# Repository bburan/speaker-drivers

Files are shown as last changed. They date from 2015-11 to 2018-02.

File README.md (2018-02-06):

# Speaker drivers (2 watt)

## Overview

This circuit can drive a small earphone speaker that requires up to 2 watts of power (e.g., 500 mA current into an 8 ohm speaker). 

* It has unity gain in a non-inverting configuration (the speakers we work with only require about 1V maximum to achieve the desired sound levels).
* High-pass input stage with 1.26 Hz cutoff (basically a DC filter).
* Two BUF634 in parallel to provide up to 500 mA of current.

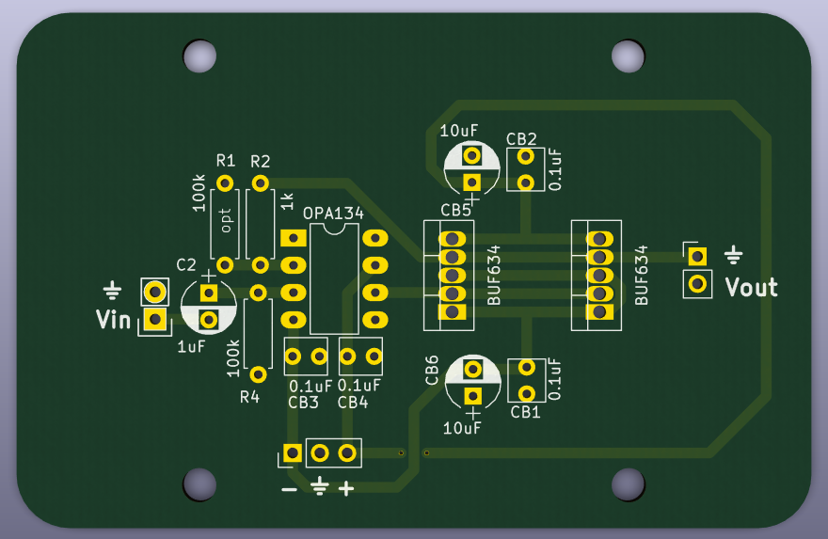
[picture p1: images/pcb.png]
Rendering of PCB


The board is 74mm x 48mm and the mounting holes, spaced 40mm x 40mm, are sized for a M3 screw. The board will fit in a Hammond enclosure that accomodates 75mm wide boards.

## Getting started

OSH Park will print and ship three of these boards for approximately $30. 

Order the parts from the [parts list](speaker%20drivers%20part%20list.md). If you get a heat sink, Aavid Thermalloy 577202B00000G should fit nicely in the space allowed.

Solder all components. Be sure to attach heat sinks to the current buffers.

Wash the board with dH<sub>2</sub>O.

## Notes

Previous iterations of the design had a high-pass filter on the output.  However, we have modified the current iteration such that the high-pass filter is found on the input stage. This allows us to eliminate bulky components (required to handle the large current) that take up a lot of space.

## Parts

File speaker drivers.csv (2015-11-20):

Reference | Value | Footprint | Datasheet
OPA1 | OPA2134 | Sockets_DIP:DIP-8__300_ELL
RL1 | 100k | Discret:R5
RL3 | 100k | Discret:R5
CLin1 | 1uF | Discret:C1
C2 | 0.1uFC | Discret:C1
C1 | 0.1uFC | Discret:C1
RR1 | 100k | Discret:R5
RR3 | 100k | Discret:R5
CRin1 | 1uF | Discret:C1
BUFR1 | BUF634 | LBHB:BUF634
CR1 | 10uFT | Capacitors_ThroughHole:Capacitor5x6RM2.5
CP3 | 0.1uFC | Discret:C1
CP2 | 10uFE | Capacitors_ThroughHole:Capacitor5x6RM2.5
CN3 | 0.1uFC | Discret:C1
CN2 | 10uFE | Capacitors_ThroughHole:Capacitor5x6RM2.5
CG2 | 10uFE | Capacitors_ThroughHole:Capacitor5x6RM2.5
RR2 | 5k | Discret:R5
RL2 | 5k | Discret:R5
BUFR2 | BUF634 | LBHB:BUF634
RR4 | 22 | Discret:R5
CR3 | 2uF | Discret:C1
LR1 | 100uH
CR2 | 10uFT | Capacitors_ThroughHole:Capacitor5x6RM2.5
BUFL1 | BUF634 | LBHB:BUF634
CL1 | 10uFT | Capacitors_ThroughHole:Capacitor5x6RM2.5
BUFL2 | BUF634 | LBHB:BUF634
RL4 | 22 | Discret:R5
CL3 | 2uF | Discret:C1
LL1 | 100uH
CL2 | 10uFT | Capacitors_ThroughHole:Capacitor5x6RM2.5
SIGIN1 | 4P_miniDIN
SER1 | 8P_miniDIN
Cvr1 | 0.33uF | Discret:C1
Cvr2 | 0.1uF | Discret:C1
SIGOUT1 | 4P_miniDIN
VREG1 | 78L05
VCTL1 | PGA2310
RS1 | 100k | Discret:R5
PWR1 | 4P_miniDIN_PWR
CR6 | 0.1uF | Discret:C1
CR5 | 0.1uF | Discret:C1
CL6 | 0.1uF | Discret:C1
CL5 | 0.1uF | Discret:C1

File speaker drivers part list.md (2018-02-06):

| References         | Number | Value         | Part number        | Note                  |
| ------------------ | ------ | ------------- | ------------------ | --------------------- |
| B1, B2             | 2      | BUF634        | BUF634T            | heat sink recommended |
| C2                 | 1      | 1uF           | MKS02-1/50/10      | metal film            |
| CB1, CB2, CB3, CB4 | 4      | 0.1uF         | RDER72A104K1S1H03A |                       |
| CB5, CB6           | 2      | 10uF          | TAP106M025SCS      | tantalum recommended  |
| J1, J2, J3, J4     | 4      | mounting hole |                    |                       |
| P1                 | 1      | 0.1" header   |                    |                       |
| P2                 | 1      | 0.1" header   |                    |                       |
| P3                 | 1      | 0.1" header   |                    |                       |
| R1, R4             | 2      | 100k          | YR1B100KCC         |                       |
| R2                 | 1      | 1k            | YR1B1K0CC          |                       |
| U1                 | 1      | OPA134        | OPA134PA           |                       |

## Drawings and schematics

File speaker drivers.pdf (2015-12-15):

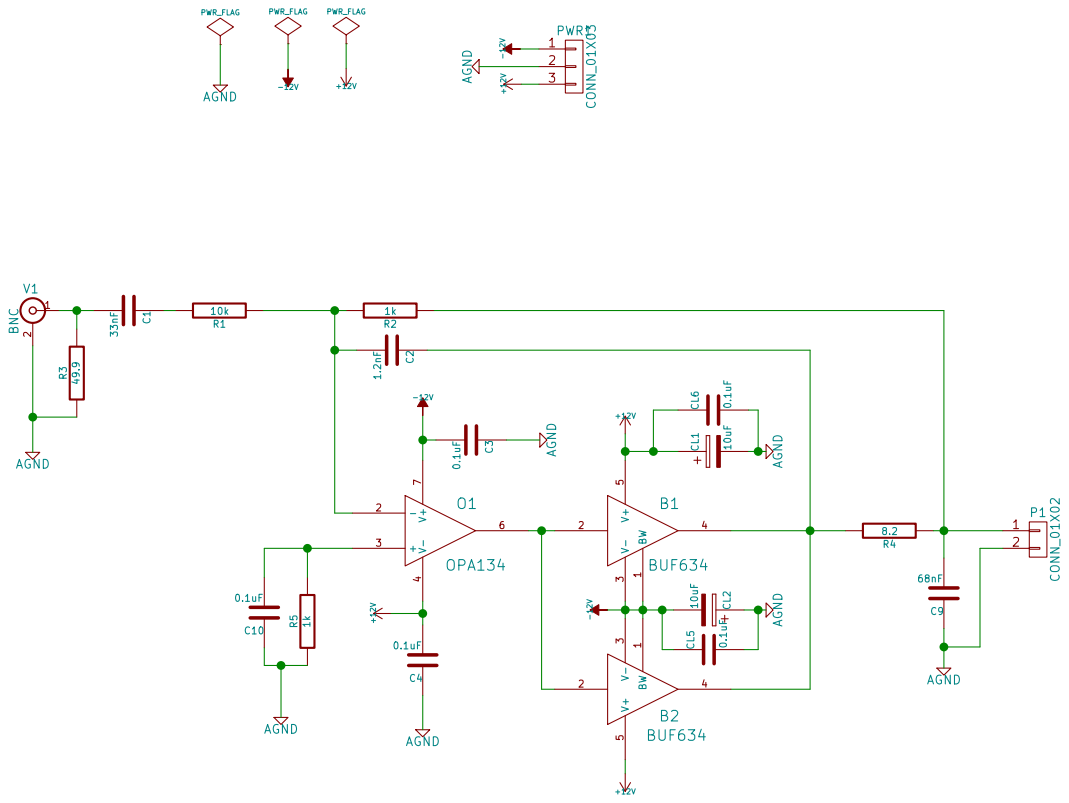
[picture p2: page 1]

This is licensed under GPLv3
File: speaker drivers.sch Sheet: / LBHB

Id: 1/1 Title: Dual Speaker Driver v2 with highpass filter

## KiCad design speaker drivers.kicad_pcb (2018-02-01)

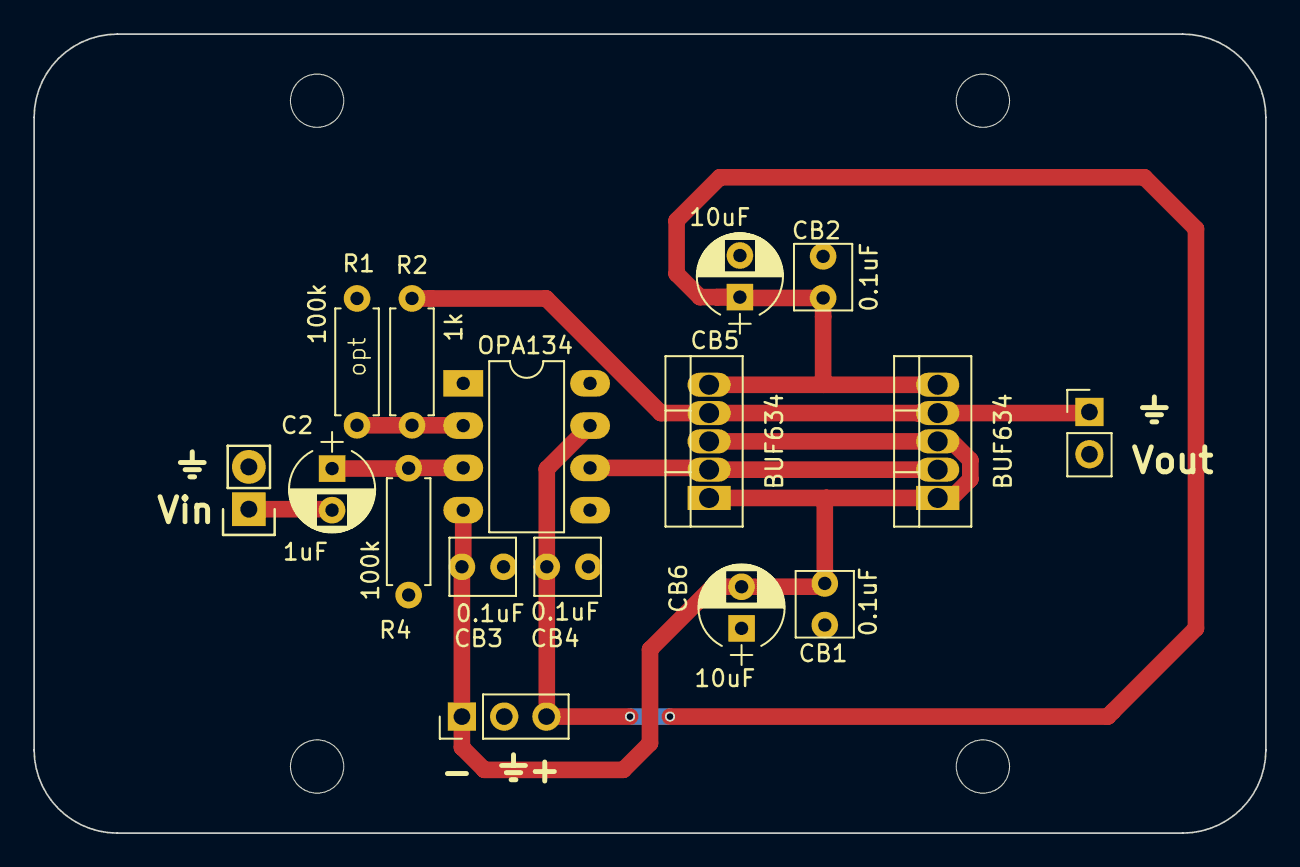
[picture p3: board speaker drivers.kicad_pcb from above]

Board: 2 copper layers, 74.0 x 48.0 mm, 20 parts (0 on the bottom side), 8 nets.

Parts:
B1: BUF634; BUF634T
B2: BUF634; TO-220-5_Vertical
C2: 1uF; CP_Radial_D5.0mm_P2.50mm
CB1, CB2, CB3, CB4: 0.1uF; C_Rect_L4.0mm_W3.5mm_P2.50mm
CB5, CB6: 10uF; CP_Radial_D5.0mm_P2.50mm
J1, J2, J3, J4: Conn_01x01; MountingHole_3.2mm_M3
P1: CONN_01X02; PinHeader_1x02_P2.54mm_Vertical
PWR1: CONN_01X03; PinHeader_1x03_P2.54mm_Vertical
R1, R4: 100k; R_Axial_DIN0207_L6.3mm_D2.5mm_P7.62mm_Horizontal
R2: 1k; R_Axial_DIN0207_L6.3mm_D2.5mm_P7.62mm_Horizontal
U1: OPA134; DIP-8_W7.62mm_LongPads
V1: BNC; Socket_Strip_Straight_1x02

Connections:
+12V: B1.5, B2.5, CB2.1, CB4.2, CB5.1, PWR1.3, U1.7
-12V: B1.1, B1.3, B2.1, B2.3, CB1.1, CB3.2, CB6.2, PWR1.1, U1.4
AGND: CB1.2, CB2.2, CB3.1, CB4.1, CB5.2, CB6.1, P1.2, PWR1.2, R1.2, R4.2, V1.2
unnamed: B1.2, B2.2, U1.6
unnamed: B1.4, B2.4, P1.1, R2.1
unnamed: C2.1, R4.1, U1.3
unnamed: C2.2, V1.1
unnamed: R1.1, R2.2, U1.2

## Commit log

2014-10-07 Initial commit of circuits for LBHB
    [speaker drivers-B_Cu.gbl, speaker drivers-B_Mask.gbs, speaker drivers-B_SilkS.gbo, speaker drivers-Edge_Cuts.gbr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]
2014-10-07 Speaker drivers V1 ready for fabrication
    [speaker drivers-B_Cu.gbl, speaker drivers-B_Mask.gbs, speaker drivers-B_SilkS.gbo, speaker drivers-Edge_Cuts.gbr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]
2014-10-07 BNC version of speaker driver V1
    [speaker drivers bnc.kicad_pcb]
2014-10-07 Fixes to speaker driver circuit
    * Ensure bypass caps between -12V and GND are correct orientation
    * Add notation for all caps indicating size
    * Widen drill holes in BUF634
    * Ensure cap symbols show orientation when needed
    [speaker drivers.kicad_pcb, speaker drivers.sch]
2014-10-09 Connect P0.0 to PFI0 ... PFI2 in speaker drivers circuit
    [speaker drivers.sch]
2015-01-07 Commit before modifying speaker driver schematic
    [speaker drivers.kicad_pcb, speaker drivers.sch]
2015-02-17 ENH: Working draft of speaker drivers v2
    [speaker drivers-B_Cu.gbl, speaker drivers-B_Mask.gbs, speaker drivers-B_SilkS.gbo, speaker drivers-Edge_Cuts.gbr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]
2015-02-17 CLN: Cleanup of speaker drivers folder
    [speaker drivers bnc.kicad_pcb]
2015-02-17 CLN: Don't track gerber folders
    [speaker drivers-B_Cu.gbl, speaker drivers-B_Mask.gbs, speaker drivers-B_SilkS.gbo, speaker drivers-Edge_Cuts.gbr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]
2015-11-20 Commit before major revisions
    [speaker drivers.csv, speaker drivers.dsn, speaker drivers.sch]
2015-11-30 WIP: Preliminary commit before splitting boards
    [speaker drivers.dsn, speaker drivers.kicad_pcb, speaker drivers.sch]
2015-12-15 WIP: Test of new circuit for speaker drivers
    Note that this circuit does not work and should not be used for
    production.
    [speaker drivers.dsn, speaker drivers.kicad_pcb, speaker drivers.sch]
2015-12-18 ENH: Revisions to speaker drivers
    [speaker drivers.kicad_pcb, speaker drivers.sch]
2018-02-01 Fixed bug in previous version and updated design
    * Inverting and noninverting inputs were swapped in the schematic. Fixed
    this bug.
    * Removed the highpass filter that follows the current buffer with a
    highpass filter at the input to the current buffer. Highpass filter
    simply removes DC offset now.
    [speaker drivers.kicad_pcb, speaker drivers.sch]
2018-02-06 Added readme
    [speaker drivers.sch]
2018-02-06 Fix image of circuit board
2018-02-06 Rename PCB image
2018-02-06 Add information on heat sink
